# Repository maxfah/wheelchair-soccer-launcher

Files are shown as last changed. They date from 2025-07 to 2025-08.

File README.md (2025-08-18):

# Wheelchair Soccer Launcher

The completed wheelchair-mounted soccer ball launcher

This project is a soccer ball launcher designed to be mounted on a wheelchair. It was developed by students from the **[Waukee APEX Program](https://apex.waukeeschools.org/)** to support the amazing work of [**Can Play**](https://can-play.org/), a nonprofit organization dedicated to providing adaptive sports and recreation opportunities for children and adults with disabilities.

The goal of this project is to provide a low-cost, accessible, and replicable design that allows more individuals to participate in wheelchair soccer.

-----

## Images & Videos

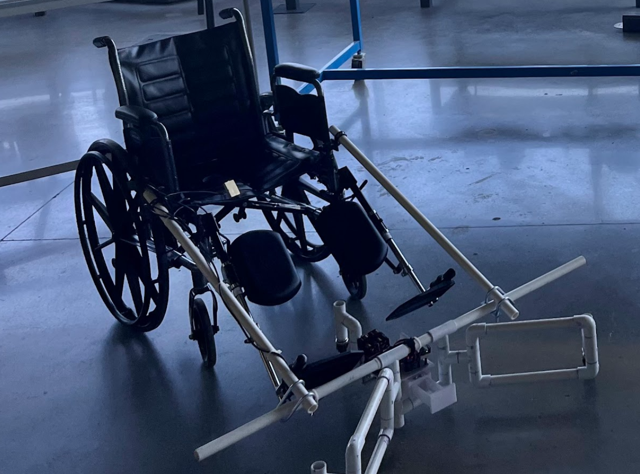
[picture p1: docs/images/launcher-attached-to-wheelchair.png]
The completed wheelchair-mounted soccer ball launcher attached to a wheelchair


All assembly images and demo videos are available below.

 * **[images](/docs/images/)**
 * **[videos](/docs/videos/)**

-----

## Documentation

All the files and instructions needed to build your own launcher can be found using the links below.

### Bill of Materials (BOM)

This document is split into two parts to make acquiring components as easy as possible. The **Project Component List** details every single part used in the final assembly. The **Purchase List** is a shopping list of the items you need to buy, often in packages that contain more parts than required for a single build.

  * **[bill-of-materials.md](/docs/bill-of-materials.md)**
  * **[bill-of-materials.xlsx](/docs/downloads/bill-of-materials.xlsx)** 

### Assembly Guide

A detailed, step-by-step guide with pictures covering the entire build process, from PVC cart assembly to final wiring.

  * **[assembly-guide.md](/docs/assembly-guide.md)**

### 3D Models

All 3D printable parts are available below. Files are available in `.step`, `.f3d`, `.3mf`, and individual `.stl` formats. The designs were created using Fusion 360.

  * **[3d-models](/3d-models/)**

### Code

All the MicroPython code for the Raspberry Pi Pico is located here. See the programming instructions in the Assembly Guide for how to load the code onto the Pico.

  * **[main.py](/micropython-code/)**

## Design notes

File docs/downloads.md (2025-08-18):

---
layout: default
title: Downloads
---

## Downloads

All the necessary design and code files for this project are available below. You can download everything in a single `.zip` package or browse the individual folders directly on GitHub.

The download includes all 3D printable parts (in `.stl`, `.step`, `.f3d`, and `.3mf` formats) designed in Fusion 360, as well as the MicroPython code for the Raspberry Pi Pico. Please see the Assembly Guide for instructions on how to load the code.

<a href="{{ site.baseurl }}/downloads/wheelchair-soccer-launcher-files.zip">Download All Project Files (.zip)</a>

---
### Browse Files on GitHub
* **3D Models:** [https://github.com/maxfah/wheelchair-soccer-launcher/tree/main/3d-models](https://github.com/maxfah/wheelchair-soccer-launcher/tree/main/3d-models)
* **MicroPython Code:** [https://github.com/maxfah/wheelchair-soccer-launcher/tree/main/micropython-code](https://github.com/maxfah/wheelchair-soccer-launcher/tree/main/micropython-code)

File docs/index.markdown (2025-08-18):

---
layout: default
---

# Wheelchair Soccer Launcher

The completed wheelchair-mounted soccer ball launcher

This project is a soccer ball launcher designed to be mounted on a wheelchair. It was developed by students from the **[Waukee APEX Program](https://apex.waukeeschools.org/)** to support the amazing work of [**Can Play**](https://can-play.org/), a nonprofit organization dedicated to providing adaptive sports and recreation opportunities for children and adults with disabilities.

The goal of this project is to provide a low-cost, accessible, and replicable design that allows more individuals to participate in wheelchair soccer.

-----

## Images & Videos

The completed wheelchair-mounted soccer ball launcher attached to a wheelchair

All assembly images and demo videos are available below.

* [**Media Gallery**](./media.html)

-----

## Documentation

All the files and instructions needed to build your own launcher can be found using the links below.

### Bill of Materials (BOM)

This document is split into two parts to make acquiring components as easy as possible. The **Project Component List** details every single part used in the final assembly. The **Purchase List** is a shopping list of the items you need to buy, often in packages that contain more parts than required for a single build.

* [**Bill of Materials**](./bill-of-materials.html)

### Assembly Guide

A detailed, step-by-step guide with pictures covering the entire build process, from PVC cart assembly to final wiring.

* [**Assembly Guide**](./assembly-guide.html)

### 3D Models & Code

All the necessary design and code files for this project can be found below. This includes all 3D printable parts (in `.stl`, `.step`, `.f3d`, and `.3mf` formats) designed in Fusion 3D, as well as the MicroPython code for the Raspberry Pi Pico. For instructions on how to load the code, please see the Assembly Guide.

* [**Downloads**](./downloads.html)

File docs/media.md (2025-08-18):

---
layout: default
title: Media Gallery
---

## Media Gallery

### Completed Project
Here are some photos of the finished launcher, both on its own and attached to a wheelchair.

<table>
  <tr>
    <td align="center">
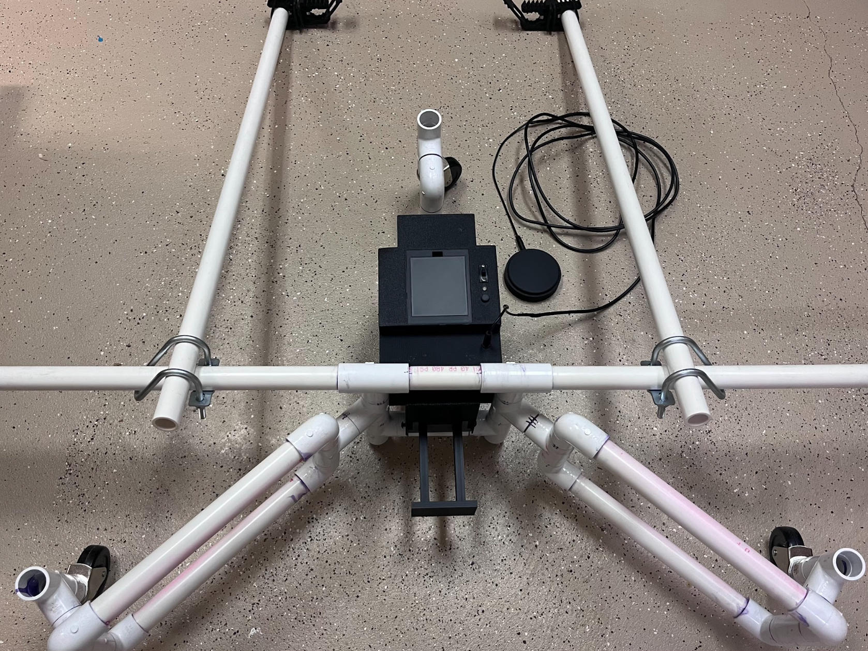
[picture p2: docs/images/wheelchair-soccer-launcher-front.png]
Finished launcher front view
      
      <br><sub>wheelchair-soccer-launcher-front.png</sub>
    </td>
    <td align="center">
      Finished launcher side view
      <br><sub>wheelchair-soccer-launcher-side.png</sub>
    </td>
    <td align="center">
      Launcher attached to a wheelchair
      <br><sub>launcher-attached-to-wheelchair.png</sub>
    </td>
  </tr>
</table>

### Videos
Here are some videos demonstrating the launcher's functionality.

**Launching a Ball**
<video width="100%" controls>
  <source src="{{ site.baseurl }}/videos/launching-ball.mp4" type="video/mp4">
  Your browser does not support the video tag.
</video>

**Testing Launcher Controls**
<video width="100%" controls>
  <source src="{{ site.baseurl }}/videos/testing-launcher-switches.mp4" type="video/mp4">
  Your browser does not support the video tag.
</video>

### Assembly Pictures
This gallery contains various pictures taken during the assembly process, showing close-ups of specific components and steps.

<table>
  <tr>
    <td align="center">
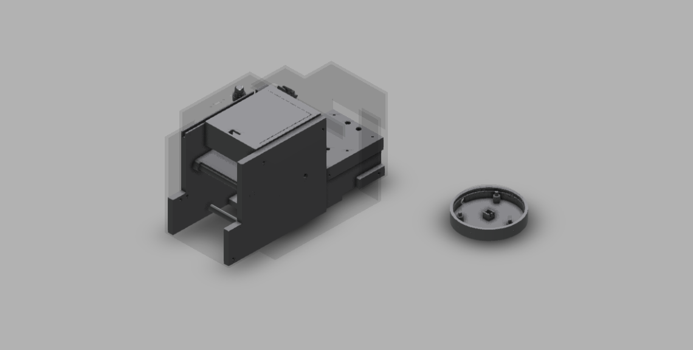
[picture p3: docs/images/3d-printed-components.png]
3D Printed Components
      
      <br><sub>3d-printed-components.png</sub>
    </td>
    <td align="center">
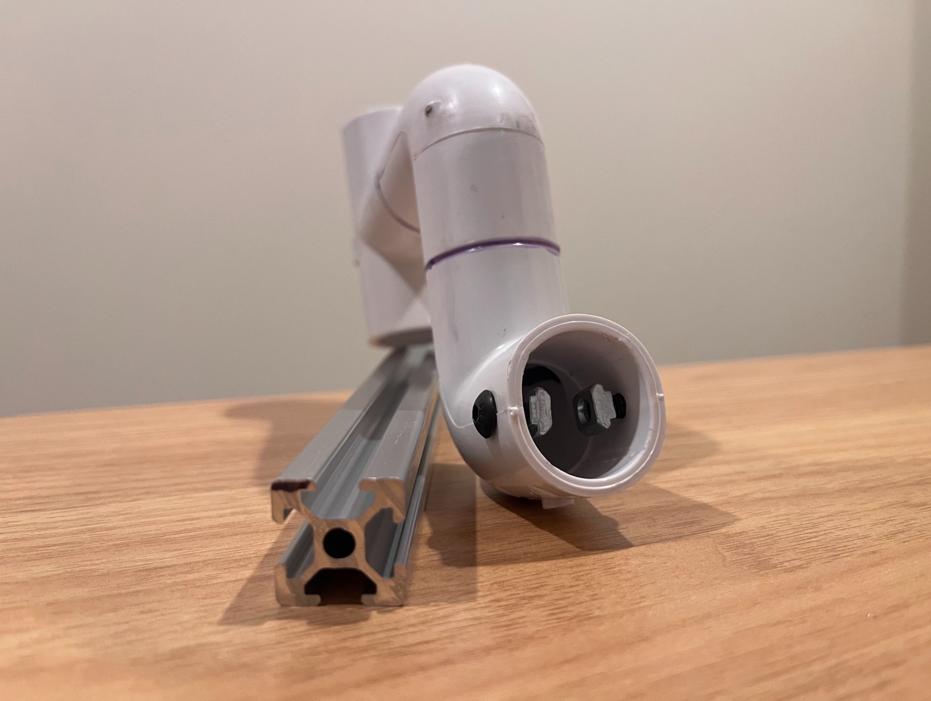
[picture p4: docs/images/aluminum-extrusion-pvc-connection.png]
Aluminum Extrusion PVC Connection
      
      <br><sub>aluminum-extrusion-pvc-connection.png</sub>
    </td>
    <td align="center">
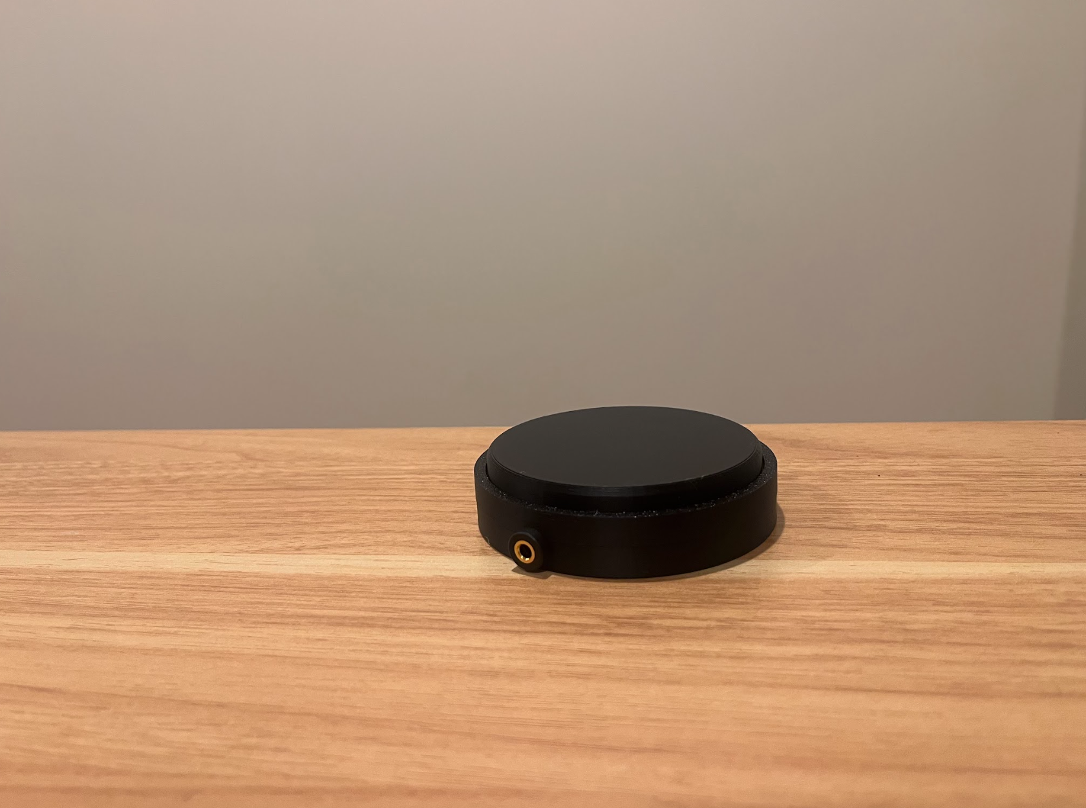
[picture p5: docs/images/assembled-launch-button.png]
Assembled Launch Button
      
      <br><sub>assembled-launch-button.png</sub>
    </td>
  </tr>
  <tr>
    <td align="center">
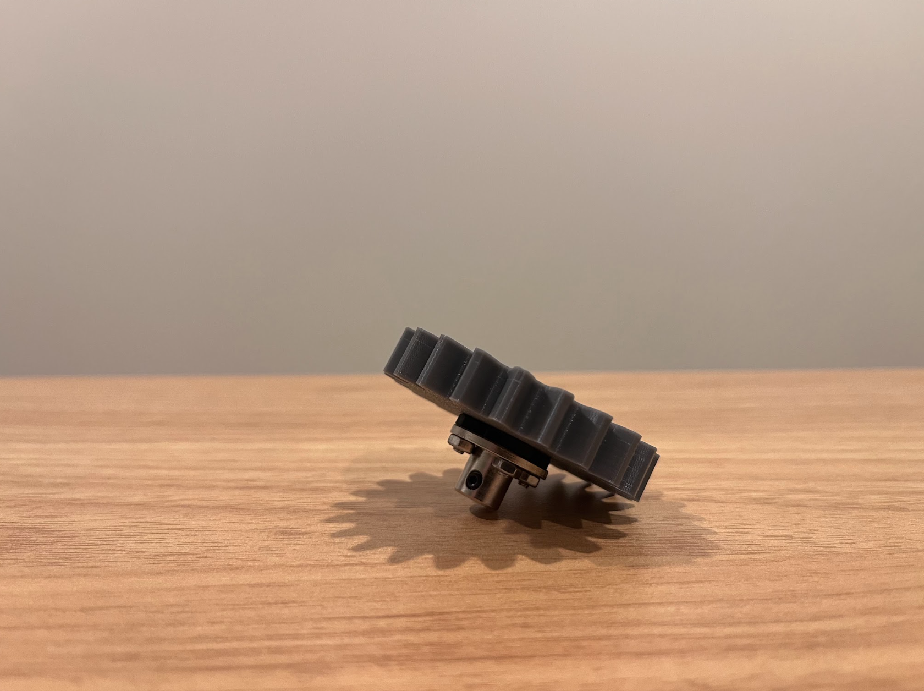
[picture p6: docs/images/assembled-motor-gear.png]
Assembled Motor Gear
      
      <br><sub>assembled-motor-gear.png</sub>
    </td>
    <td align="center">
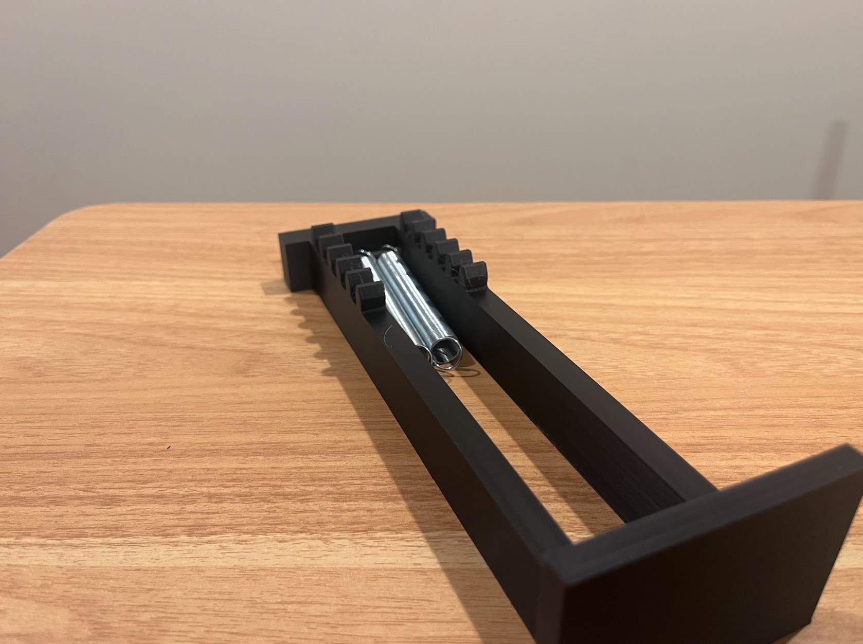
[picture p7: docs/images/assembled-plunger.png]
Assembled Plunger
      
      <br><sub>assembled-plunger.png</sub>
    </td>
    <td align="center">
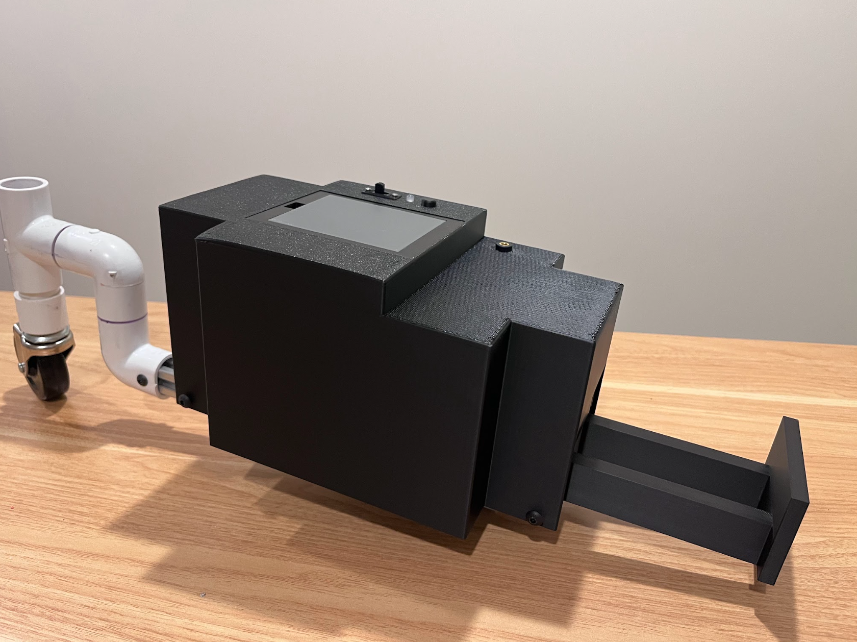
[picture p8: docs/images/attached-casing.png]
Attached Casing
      
      <br><sub>attached-casing.png</sub>
    </td>
  </tr>
  <tr>
    <td align="center">
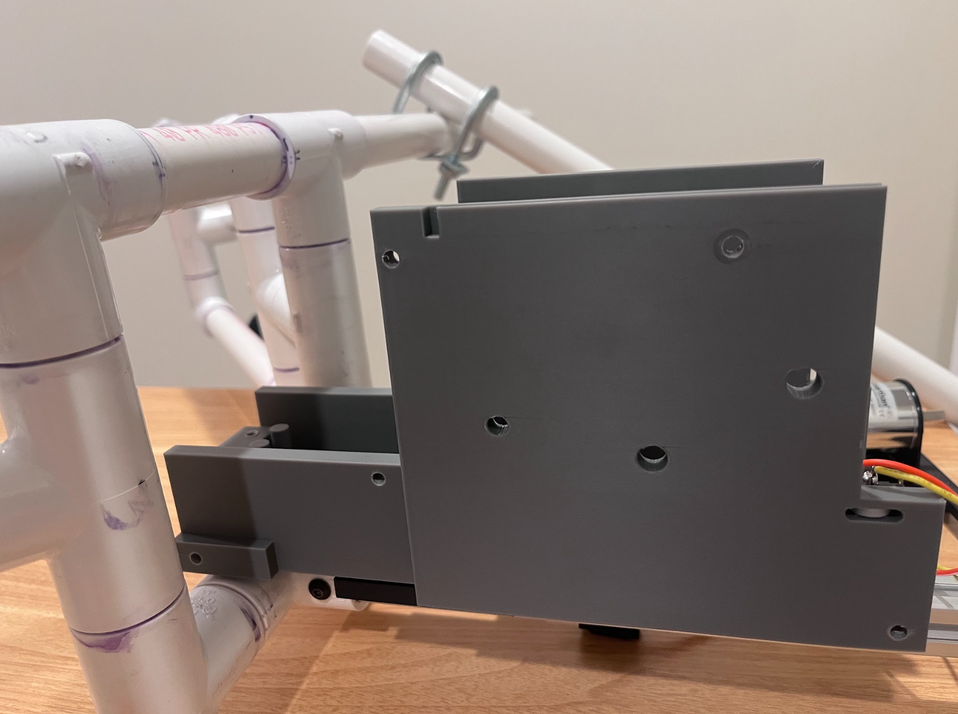
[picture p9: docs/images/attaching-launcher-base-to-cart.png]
Attaching Launcher Base to Cart
      
      <br><sub>attaching-launcher-base-to-cart.png</sub>
    </td>
    <td align="center">
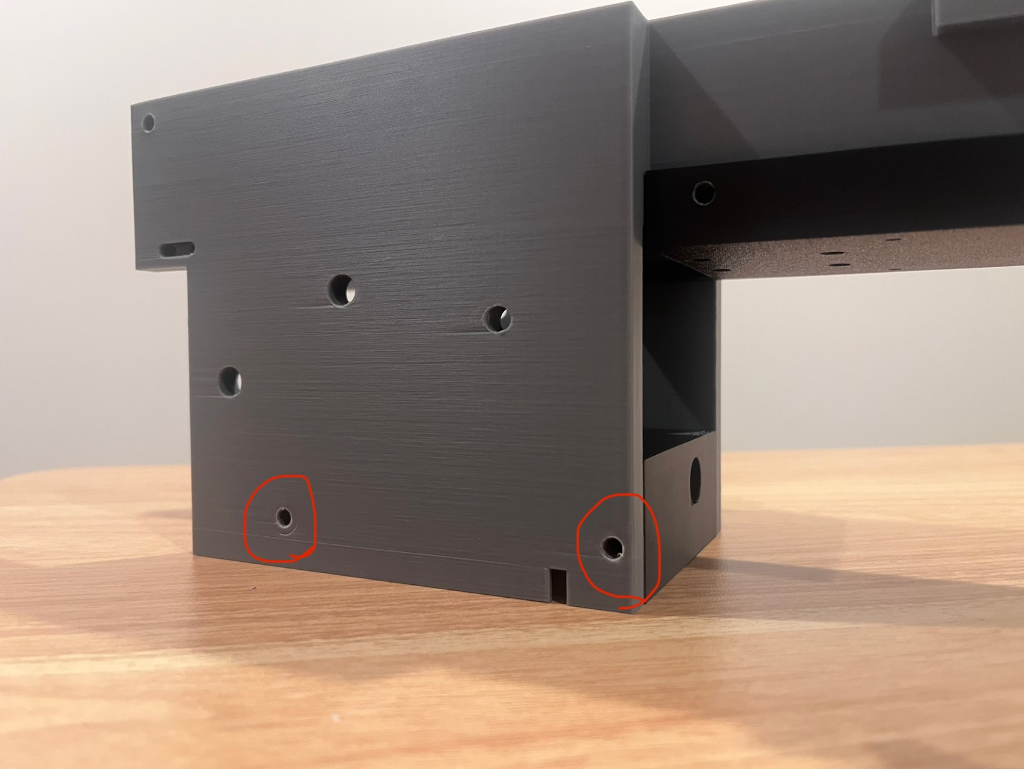
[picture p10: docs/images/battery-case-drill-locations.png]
Battery Case Drill Locations
      
      <br><sub>battery-case-drill-locations.png</sub>
    </td>
    <td align="center">
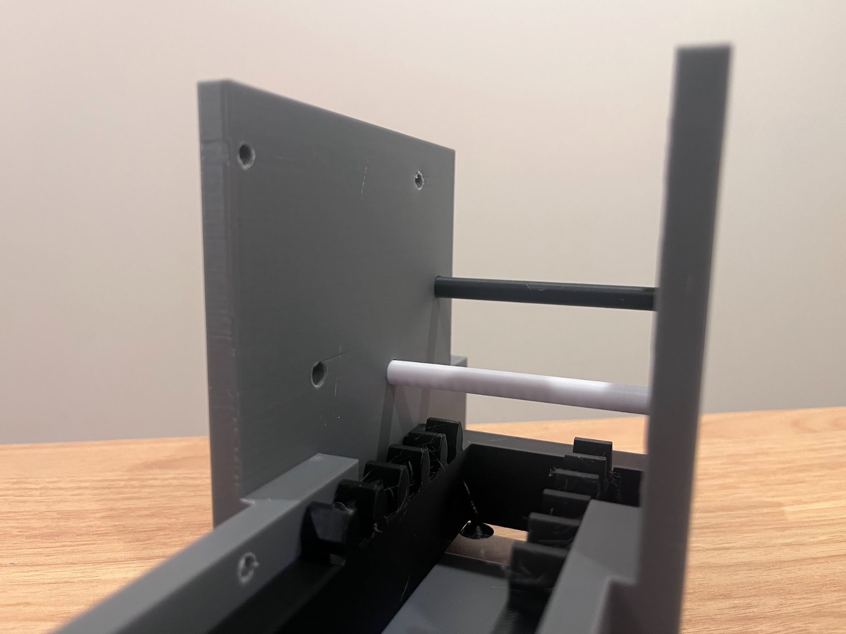
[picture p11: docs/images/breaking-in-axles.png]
Breaking In Axles
      
      <br><sub>breaking-in-axles.png</sub>
    </td>
  </tr>
  <tr>
    <td align="center">
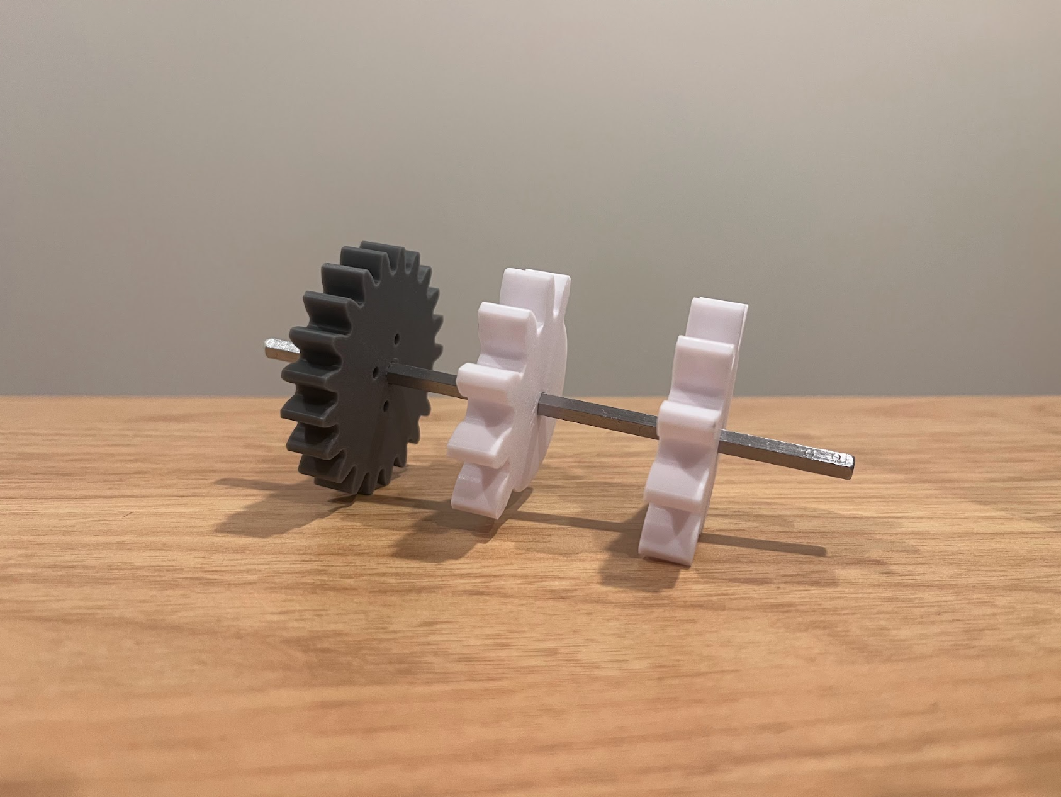
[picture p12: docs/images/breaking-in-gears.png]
Breaking In Gears
      
      <br><sub>breaking-in-gears.png</sub>
    </td>
    <td align="center">
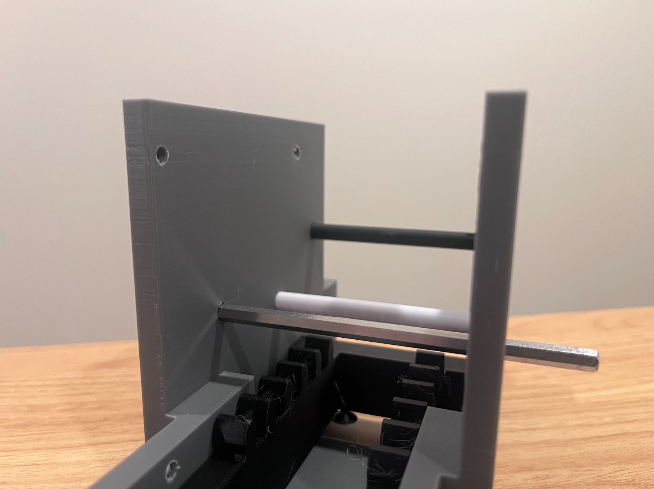
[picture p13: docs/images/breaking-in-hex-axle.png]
Breaking In Hex Axle
      
      <br><sub>breaking-in-hex-axle.png</sub>
    </td>
    <td align="center">
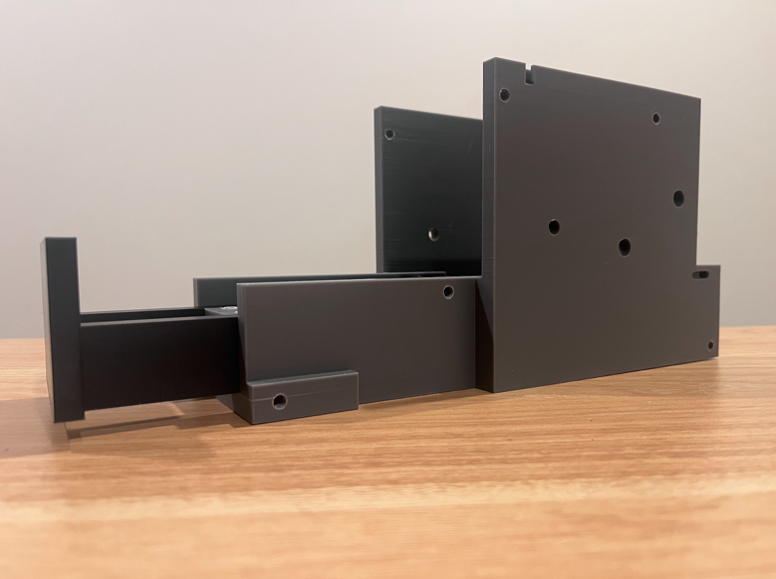
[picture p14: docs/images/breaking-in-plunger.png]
Breaking In Plunger
      
      <br><sub>breaking-in-plunger.png</sub>
    </td>
  </tr>
  <tr>
    <td align="center">
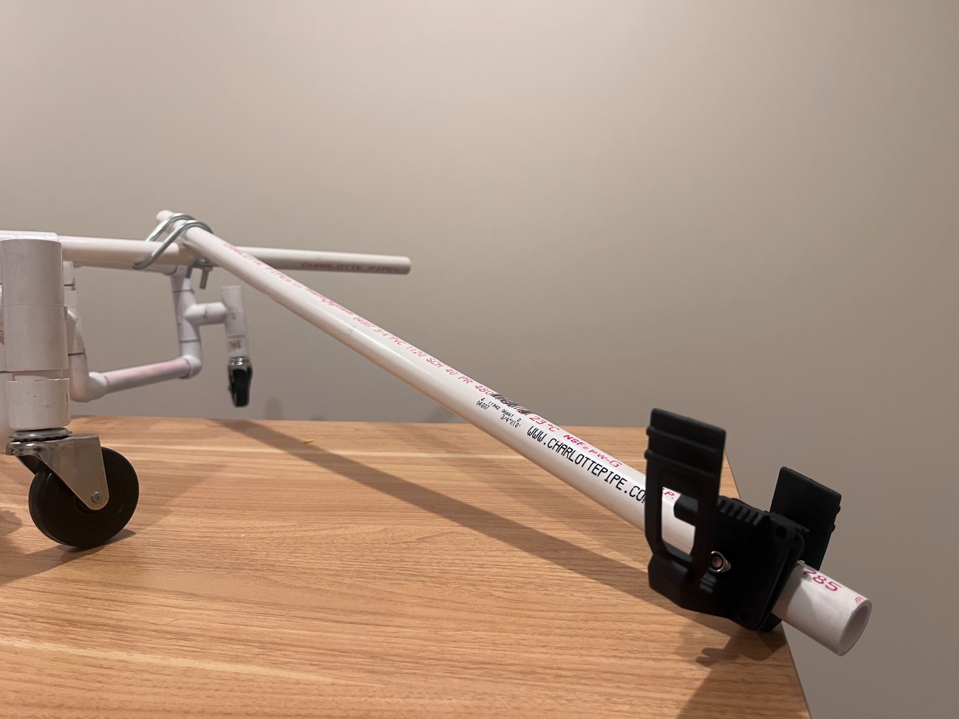
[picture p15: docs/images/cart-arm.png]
Cart Arm
      
      <br><sub>cart-arm.png</sub>
    </td>
    <td align="center">
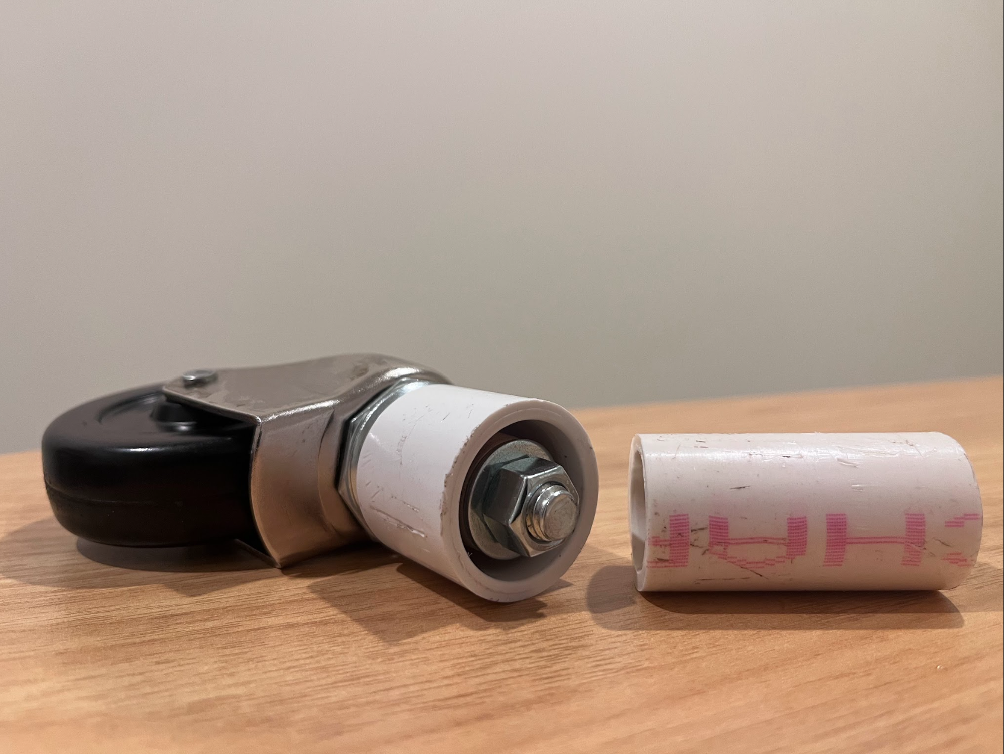
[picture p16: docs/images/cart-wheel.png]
Cart Wheel
      
      <br><sub>cart-wheel.png</sub>
    </td>
    <td align="center">
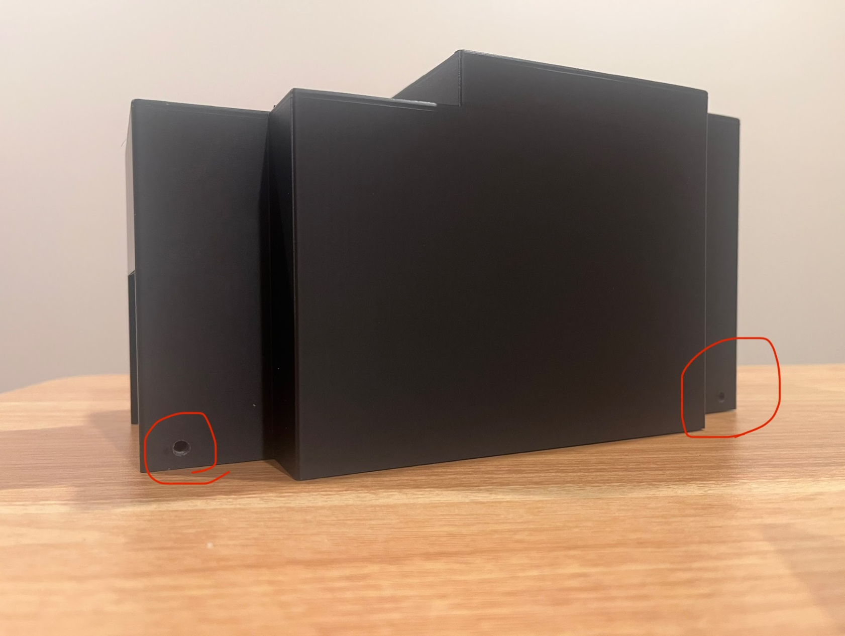
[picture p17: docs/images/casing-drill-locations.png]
Casing Drill Locations
      
      <br><sub>casing-drill-locations.png</sub>
    </td>
  </tr>
  <tr>
    <td align="center">
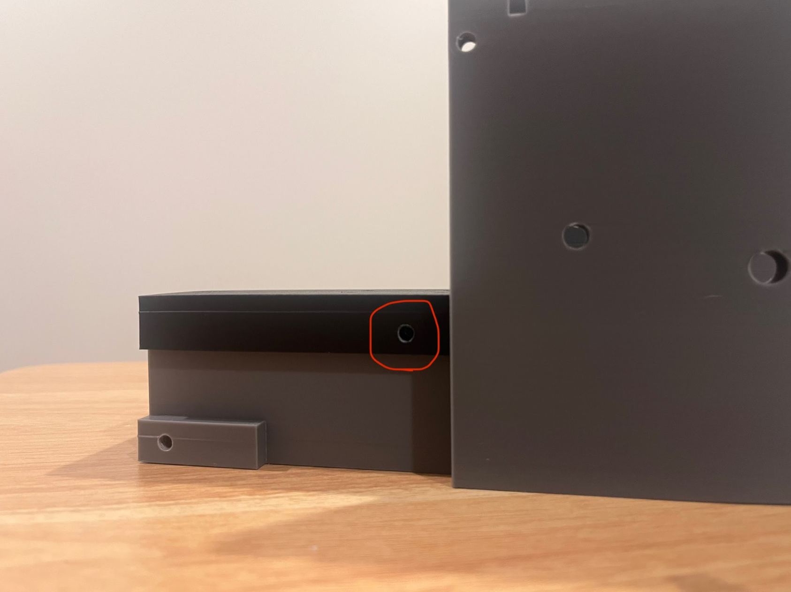
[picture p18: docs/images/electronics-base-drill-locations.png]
Electronics Base Drill Locations
      
      <br><sub>electronics-base-drill-locations.png</sub>
    </td>
    <td align="center">
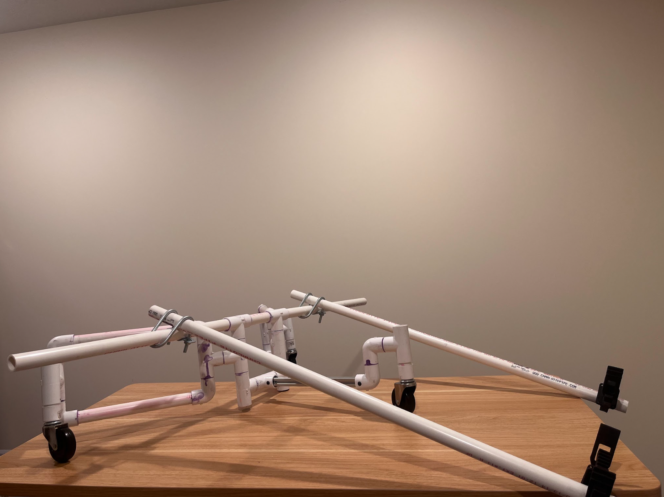
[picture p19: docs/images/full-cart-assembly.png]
Full Cart Assembly
      
      <br><sub>full-cart-assembly.png</sub>
    </td>
    <td align="center">
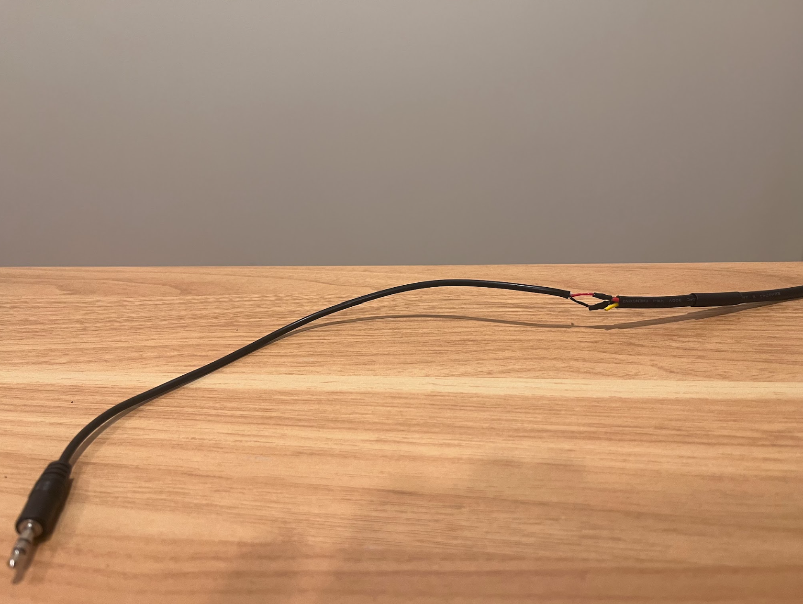
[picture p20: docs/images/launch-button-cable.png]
Launch Button Cable
      
      <br><sub>launch-button-cable.png</sub>
    </td>
  </tr>
  <tr>
    <td align="center">
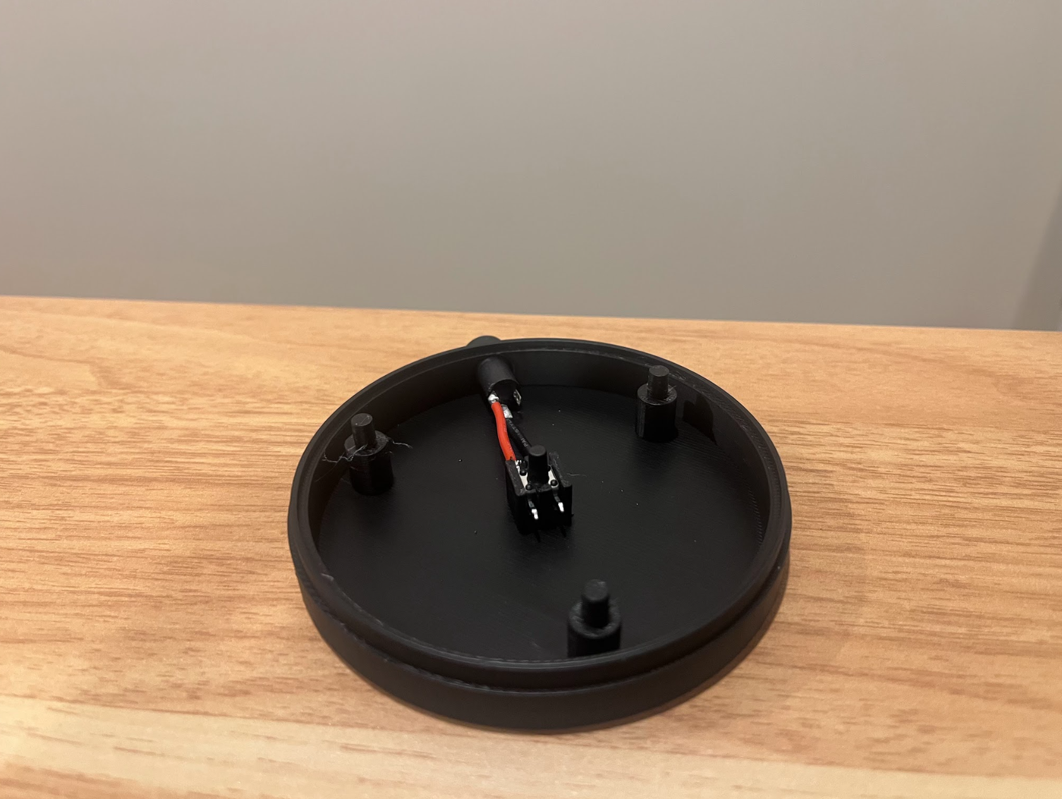
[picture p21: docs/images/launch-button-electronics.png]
Launch Button Electronics
      
      <br><sub>launch-button-electronics.png</sub>
    </td>
    <td align="center">
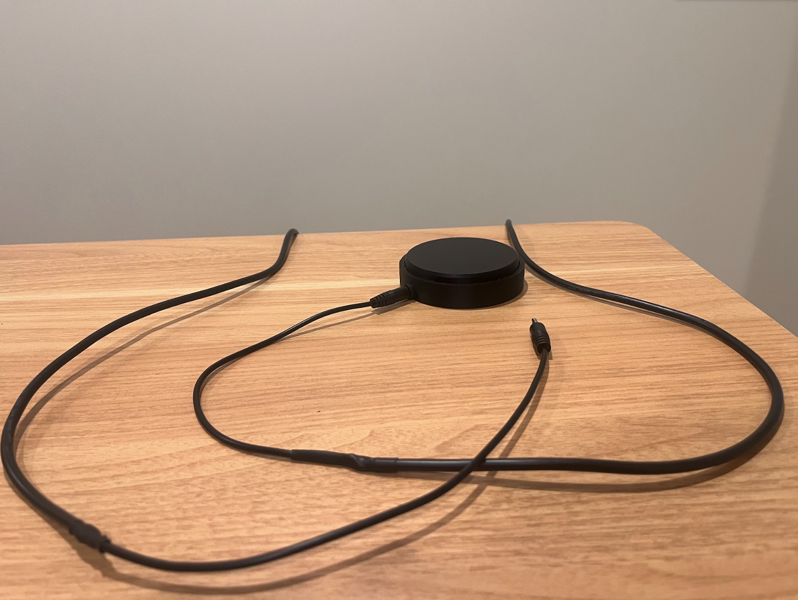
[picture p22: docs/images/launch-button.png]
Launch Button
      
      <br><sub>launch-button.png</sub>
    </td>
    <td align="center">
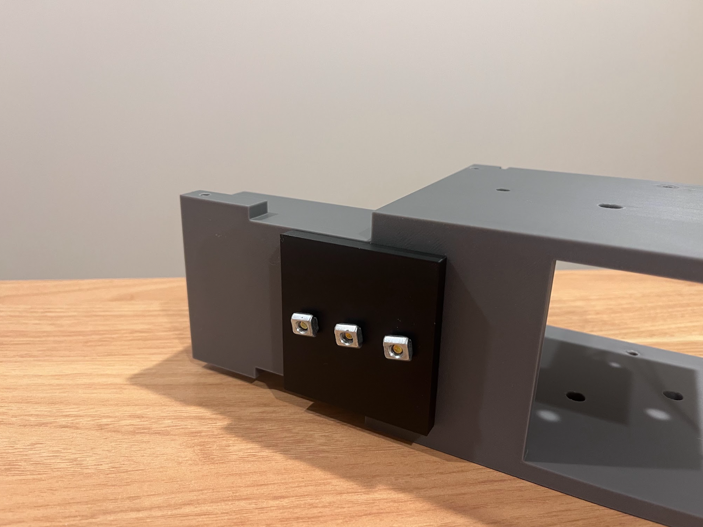
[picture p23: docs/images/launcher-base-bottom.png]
Launcher Base Bottom
      
      <br><sub>launcher-base-bottom.png</sub>
    </td>
  </tr>
  <tr>
    <td align="center">
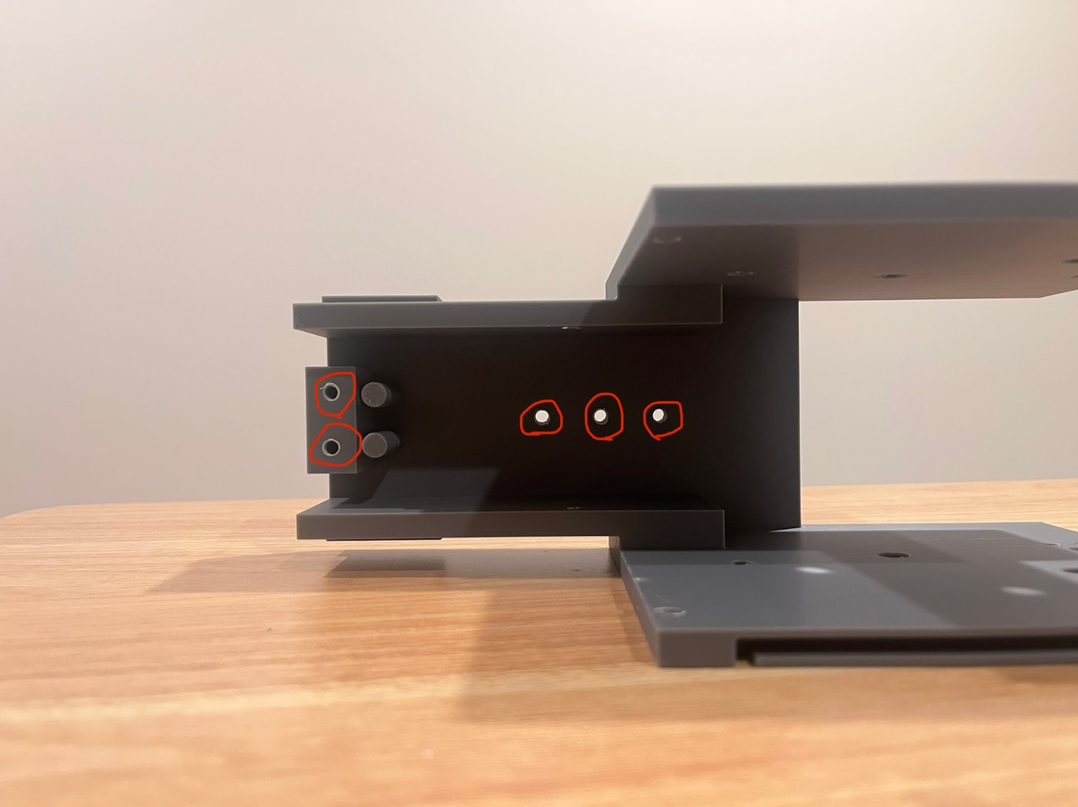
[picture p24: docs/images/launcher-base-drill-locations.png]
Launcher Base Drill Locations
      
      <br><sub>launcher-base-drill-locations.png</sub>
    </td>
    <td align="center">
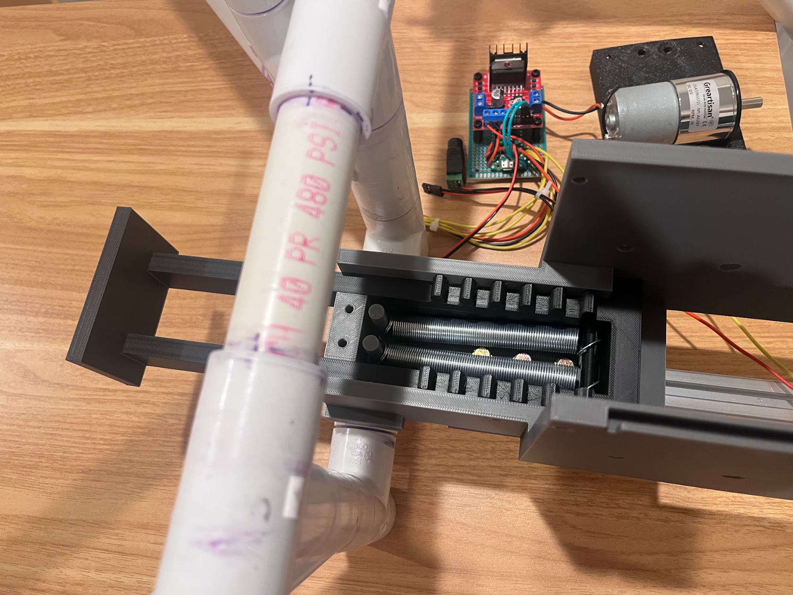
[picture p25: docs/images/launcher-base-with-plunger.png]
Launcher Base with Plunger
      
      <br><sub>launcher-base-with-plunger.png</sub>
    </td>
    <td align="center">
      Launcher Circuit
      <br><sub>launcher-circuit.png</sub>
    </td>
  </tr>
  <tr>
    <td align="center">
      Main Cart Frame Design
      <br><sub>main-cart-frame-design.png</sub>
    </td>
    <td align="center">
      Main Control Board
      <br><sub>main-control-board.png</sub>
    </td>
    <td align="center">
      Mounted Batteries
      <br><sub>mounted-batteries.png</sub>
    </td>
  </tr>
  <tr>
    <td align="center">
      Mounted Battery Case
      <br><sub>mounted-battery-case.png</sub>
    </td>
    <td align="center">
      Mounted Control Board
      <br><sub>mounted-control-board.png</sub>
    </td>
    <td align="center">
      Mounted Electronics Base
      <br><sub>mounted-electronics-base.png</sub>
    </td>
  </tr>
  <tr>
    <td align="center">
      Mounted Hex Shaft
      <br><sub>mounted-hex-shaft.png</sub>
    </td>
    <td align="center">
      Mounted Motor Gear
      <br><sub>mounted-motor-gear.png</sub>
    </td>
    <td align="center">
      Mounted Pawl
      <br><sub>mounted-pawl.png</sub>
    </td>
  </tr>
  <tr>
    <td align="center">
      Mounting Limit Switch
      <br><sub>mounting-limit-switch.png</sub>
    </td>
    <td align="center">
      Mounting Motor
      <br><sub>mounting-motor.png</sub>
    </td>
    <td align="center">
      PVC Drill Locations
      <br><sub>pvc-drill-locations.png</sub>
    </td>
  </tr>
  <tr>
    <td align="center">
      Testing Electronics
      <br><sub>testing-electronics.png</sub>
    </td>
    <td align="center">
      Wheelchair Grip
      <br><sub>wheelchair-grip.png</sub>
    </td>
    <td align="center">
      Wiring Casing
      <br><sub>wiring-casing.png</sub>
    </td>
  </tr>
  <tr>
    <td align="center">
      Wiring L298N
      <br><sub>wiring-l298n.png</sub>
    </td>
    <td align="center">
      Wiring Pico
      <br><sub>wiring-pico.png</sub>
    </td>
    <td align="center">
    </td>
  </tr>
</table>

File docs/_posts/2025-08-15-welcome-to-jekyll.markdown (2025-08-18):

---
layout: post
title:  "Welcome to Jekyll!"
date:   2025-08-15 19:27:29 -0500
categories: jekyll update
---
You’ll find this post in your `_posts` directory. Go ahead and edit it and re-build the site to see your changes. You can rebuild the site in many different ways, but the most common way is to run `jekyll serve`, which launches a web server and auto-regenerates your site when a file is updated.

Jekyll requires blog post files to be named according to the following format:

`YEAR-MONTH-DAY-title.MARKUP`

Where `YEAR` is a four-digit number, `MONTH` and `DAY` are both two-digit numbers, and `MARKUP` is the file extension representing the format used in the file. After that, include the necessary front matter. Take a look at the source for this post to get an idea about how it works.

Jekyll also offers powerful support for code snippets:

{% highlight ruby %}
def print_hi(name)
  puts "Hi, #{name}"
end
print_hi('Tom')
#=> prints 'Hi, Tom' to STDOUT.
{% endhighlight %}

Check out the [Jekyll docs][jekyll-docs] for more info on how to get the most out of Jekyll. File all bugs/feature requests at [Jekyll’s GitHub repo][jekyll-gh]. If you have questions, you can ask them on [Jekyll Talk][jekyll-talk].

[jekyll-docs]: https://jekyllrb.com/docs/home
[jekyll-gh]:   https://github.com/jekyll/jekyll
[jekyll-talk]: https://talk.jekyllrb.com/

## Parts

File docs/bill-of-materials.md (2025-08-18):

---
layout: default
title: Bill of Materials
---

## Project Component List

This list details every individual component required for the project, along with its calculated cost based on the package price.

<a href="{{ site.baseurl }}/downloads/bill-of-materials.xlsx">Download Original Spreadsheet (.xlsx)</a>

### Electronics

| Item | Source | Quantity | Unit of Measure | Unit Cost | Total Project Cost |
| :--- | :--- | :--- | :--- | :--- | :--- |
| 11' 20 AWG 3-Conductor Electrical Wire | [33' 20 AWG 3-Conductor Electrical Wire](https://a.co/d/fJsRZCa) | 1 | ea | $5.33 | $5.33 |
| 18650 Battery Case Holder | [18650 Battery Case Holder](https://a.co/d/0sHe8RC) | 1 | ea | $4.00 | $4.00 |
| 18650 Rechargeable Batteries | [18650 Rechargeable Batteries with Charger (4-pack)](https://a.co/d/61mFCPq) | 3 | ea | $5.50 | $16.50 |
| 2 Pin Housing Connector | [Dupont Connector Kit (600 pcs)](https://a.co/d/eYwAEnl) | 1 | ea | $0.02 | $0.02 |
| 3.5mm Female Mount Jack | [3.5mm Female Mount Jack (3-pack)](https://a.co/d/40ZtWEH) | 2 | ea | $2.33 | $4.66 |
| 3.5mm Male Plug Jack Connector | [3.5mm Male Jack Connector (2-pack)](https://a.co/d/iWRQpHo) | 2 | ea | $2.75 | $5.50 |
| 470 Ω Resistor | [470 Ω Resistors (100 pcs)](https://a.co/d/aYIXwVM) | 1 | ea | $0.06 | $0.06 |
| 5 Pin Housing Connector | [Dupont Connector Kit (600 pcs)](https://a.co/d/eYwAEnl) | 2 | ea | $0.02 | $0.04 |
| 5.5mm Female DC Barrel Connector | [12V 2.1mm x 5.5mm DC Power Jack Adapter (4-pack)](https://a.co/d/751q0LK) | 1 | ea | $0.99 | $0.99 |
| 5cm x 7cm PCB Board | [PCB Boards (32 pcs)](https://a.co/d/8yXHcdF) | 1 | ea | $0.22 | $0.22 |
| DC Motor | [Greartisan DC 12V 30RPM Gear Motor](https://a.co/d/9EDaZ5f) | 1 | ea | $15.99 | $15.99 |
| Female Pin Connector | [Dupont Connector Kit (600 pcs)](https://a.co/d/eYwAEnl) | 7 | ea | $0.02 | $0.14 |
| Limit Switch | [Micro Limit Switch (1-pack)](https://a.co/d/icHqxsF) | 1 | ea | $3.99 | $3.99 |
| Male Pin Connector | [Dupont Connector Kit (600 pcs)](https://a.co/d/eYwAEnl) | 5 | ea | $0.02 | $0.10 |
| L298N Motor Driver | [L298N H Bridge Stepper Motor Driver](https://a.co/d/d2QPwzO) | 1 | ea | $2.50 | $2.50 |
| Raspberry Pi Pico | [Raspberry Pi Pico H - Pico with Headers Soldered](https://www.adafruit.com/product/5525) | 1 | ea | $5.00 | $5.00 |
| RGB 5mm LED | [RGB 5mm Tri-Color LEDs](https://a.co/d/4jlZoVg) | 1 | ea | $0.09 | $0.09 |
| Slide Switch | [Compact Slide Switch](https://a.co/d/2EBehJg) | 1 | ea | $3.99 | $3.99 |
| 6x6x9.5mm Tactile Push Button Switch | [Tactile Push Button Switches (180 pcs)](https://a.co/d/5Mcb5Zq) | 1 | ea | $0.05 | $0.05 |
| 6x6x11mm Tactile Push Button Switch | [Tactile Push Button Switches (180 pcs)](https://a.co/d/5Mcb5Zq) | 1 | ea | $0.05 | $0.05 |

### Fasteners & Hardware

| Item | Source | Quantity | Unit of Measure | Unit Cost | Total Project Cost |
| :--- | :--- | :--- | :--- | :--- | :--- |
| 3/8"-16 Coarse Thread Hex Nut | [3/8"-16 Zinc Plated Coarse Thread Hex Nut (8-pack)](https://www.menards.com/main/hardware/fasteners-connectors/nuts/hex-jam-nuts/grip-fast-reg-blue-zinc-grade-2-coarse-thread-hex-nuts/zhn38-8/p-1444421582846-c-8915.htm) | 3 | ea | $0.13 | $0.39 |
| 3/8" Flat Washer | [3/8" Zinc Plated Flat Washer (24-pack)](https://www.menards.com/main/hardware/fasteners-connectors/washers-spacers/flat-washers/grip-fast-reg-3-8-grade-2-a307-zinc-flat-washer-24-count/15073/p-1444439719658-c-8945.htm) | 3 | ea | $0.07 | $0.21 |
| M3 (15mm + 6mm) Single Head Standoff | [M3 Standoff Kit (320 pcs)](https://a.co/d/gYZp2mI) | 2 | ea | $0.03 | $0.06 |
| M3 (15mm) Double-Pass Standoff | [M3 Standoff Kit (320 pcs)](https://a.co/d/gYZp2mI) | 6 | ea | $0.03 | $0.18 |
| M3 Coupler Fastening Screw | [6mm Flange Shaft Coupler (5-pack)](https://a.co/d/dtI1bwZ) | 3 | ea | $0.20 | $0.60 |
| M3 Coupler Nut | [6mm Flange Shaft Coupler (5-pack)](https://a.co/d/dtI1bwZ) | 4 | ea | $0.20 | $0.80 |
| M3 Standoff Nut | [M3 Standoff Kit (320 pcs)](https://a.co/d/gYZp2mI) | 4 | ea | $0.03 | $0.12 |
| M3 x 12mm Standoff Screw | [M3 Standoff Kit (320 pcs)](https://a.co/d/gYZp2mI) | 4 | ea | $0.03 | $0.12 |
| M3 x 14mm Coupler Socket Head Cap Screw | [6mm Flange Shaft Coupler (5-pack)](https://a.co/d/dtI1bwZ) | 4 | ea | $0.20 | $0.80 |
| M3 x 6mm Standoff Screw | [M3 Standoff Kit (320 pcs)](https://a.co/d/gYZp2mI) | 8 | ea | $0.03 | $0.24 |
| M3 Washer | [M3 Standoff Kit (320 pcs)](https://a.co/d/gYZp2mI) | 4 | ea | $0.03 | $0.12 |
| M5 Flat Washer | [Assorted Nuts and Bolts Kit (720 pcs)](https://www.amazon.com/720pcs-Metric-Assortment-Yellow-Plated/dp/B0BYNLV7YG?ref_=ast_sto_dp&th=1) | 5 | ea | $0.04 | $0.20 |
| M5 Nut | [Assorted Nuts and Bolts Kit (720 pcs)](https://www.amazon.com/720pcs-Metric-Assortment-Yellow-Plated/dp/B0BYNLV7YG?ref_=ast_sto_dp&th=1) | 4 | ea | $0.04 | $0.16 |
| M5 T Nut | [M5 Screws and T Nuts Kit (420 pcs)](https://a.co/d/blOClPc) | 7 | ea | $0.04 | $0.28 |
| M5 x 8mm Screw | [M5 Screws and T Nuts Kit (420 pcs)](https://a.co/d/blOClPc) | 6 | ea | $0.04 | $0.24 |
| M5 x 10mm Screw | [M5 Screws and T Nuts Kit (420 pcs)](https://a.co/d/blOClPc) | 4 | ea | $0.04 | $0.16 |
| M5 x 12mm Screw | [M5 Screws and T Nuts Kit (420 pcs)](https://a.co/d/blOClPc) | 4 | ea | $0.04 | $0.16 |
| M5 x 14mm Screw | [M5 Screws and T Nuts Kit (420 pcs)](https://a.co/d/blOClPc) | 4 | ea | $0.04 | $0.16 |
| M5 x 25mm Bolt | [Assorted Nuts and Bolts Kit (720 pcs)](https://www.amazon.com/720pcs-Metric-Assortment-Yellow-Plated/dp/B0BYNLV7YG?ref_=ast_sto_dp&th=1) | 3 | ea | $0.04 | $0.12 |
| M5 x 30mm Bolt | [Assorted Nuts and Bolts Kit (720 pcs)](https://www.amazon.com/720pcs-Metric-Assortment-Yellow-Plated/dp/B0BYNLV7YG?ref_=ast_sto_dp&th=1) | 2 | ea | $0.04 | $0.08 |
| M6 Flat Washer | [Assorted Nuts and Bolts Kit (720 pcs)](https://www.amazon.com/720pcs-Metric-Assortment-Yellow-Plated/dp/B0BYNLV7YG?ref_=ast_sto_dp&th=1) | 6 | ea | $0.04 | $0.24 |
| M6 Nylon Lock Nut | [M6 x 1mm Nylon Lock Nuts (35 pcs)](https://a.co/d/dPlYyLJ) | 2 | ea | $0.16 | $0.32 |
| M6 x 30mm Bolt | [Assorted Nuts and Bolts Kit (720 pcs)](https://www.amazon.com/720pcs-Metric-Assortment-Yellow-Plated/dp/B0BYNLV7YG?ref_=ast_sto_dp&th=1) | 2 | ea | $0.04 | $0.08 |

### Structural & Mechanical

| Item | Source | Quantity | Unit of Measure | Unit Cost | Total Project Cost |
| :--- | :--- | :--- | :--- | :--- | :--- |
| 1/2" x 3-13/16" Extension Springs | [1/2" x 3-13/16" Zinc Extension Spring](https://www.menards.com/main/hardware/fasteners-connectors/specialty-fasteners/springs/midwest-fastener-reg-1-2-x-3-13-16-zinc-extension-spring-1-count/88121/p-1444440197466-c-9553.htm) | 2 | ea | $2.39 | $4.78 |
| 11.8" (300mm) 200 T Slot Aluminum Extrusion | [300mm 2020 T Slot Aluminum Extrusions (4 pcs)](https://a.co/d/22snyCf) | 1 | ea | $6.00 | $6.00 |
| 2-1/2" Soft Rubber Swivel Caster Wheel | [2-1/2" Soft Rubber Swivel Caster Wheel w/ 3/8"-16 x 1-1/2" threaded swivel stem](https://www.menards.com/main/hardware/casters-furniture-hardware/casters/shepherd-hardware-reg-2-1-2-soft-rubber-swivel-caster-wheel/9340m/p-1444442245967-c-13090.htm?exp=false) | 3 | ea | $4.49 | $13.47 |
| 3/4" x 1" Wood Dowel | [3/4" x 48" Round Poplar Dowel](https://www.menards.com/main/doors-windows-millwork/dowels-wooden-pins-plugs/madison-mill-round-poplar-dowels/436578/p-1444438758494-c-12188.htm) | 3 | ea | $0.07 | $0.21 |
| 3/4" x 11" PVC Pipe | [3/4" x 10' SDR 21 PVC Plain End Pressure Pipe](https://www.menards.com/main/plumbing/pipe-fittings/pvc-pipe-fittings/sdr21-pvc-pressure-pipe/pvc200070600hc/p-1444426399617-c-8571.htm?missingVariation=true) | 4 | ea | $0.39 | $1.56 |
| 3/4" x 2" PVC Pipe | [3/4" x 10' SDR 21 PVC Plain End Pressure Pipe](https://www.menards.com/main/plumbing/pipe-fittings/pvc-pipe-fittings/sdr21-pvc-pressure-pipe/pvc200070600hc/p-1444426399617-c-8571.htm?missingVariation=true) | 23 | ea | $0.07 | $1.61 |
| 3/4" x 20" PVC Pipe | [3/4" x 10' SDR 21 PVC Plain End Pressure Pipe](https://www.menards.com/main/plumbing/pipe-fittings/pvc-pipe-fittings/sdr21-pvc-pressure-pipe/pvc200070600hc/p-1444426399617-c-8571.htm?missingVariation=true) | 2 | ea | $0.72 | $1.44 |
| 3/4" x 36" PVC Pipe | [3/4" x 10' SDR 21 PVC Plain End Pressure Pipe](https://www.menards.com/main/plumbing/pipe-fittings/pvc-pipe-fittings/sdr21-pvc-pressure-pipe/pvc200070600hc/p-1444426399617-c-8571.htm?missingVariation=true) | 2 | ea | $1.29 | $2.58 |
| 3/4" x 5" PVC Pipe | [3/4" x 10' SDR 21 PVC Plain End Pressure Pipe](https://www.menards.com/main/plumbing/pipe-fittings/pvc-pipe-fittings/sdr21-pvc-pressure-pipe/pvc200070600hc/p-1444426399617-c-8571.htm?missingVariation=true) | 1 | ea | $0.18 | $0.18 |
| 3/4" Socket PVC 90-Degree Elbow | [3/4" Socket Sch 40 PVC 90-Degree Elbow](https://www.menards.com/main/plumbing/pipe-fittings/pvc-pipe-fittings/nibco-reg-socket-schedule-40-pvc-90-degree-elbow/f01680d/p-1444449163717-c-8571.htm?exp=false) | 10 | ea | $0.67 | $6.70 |
| 3/4" Socket PVC Cap | [3/4" Socket Sch 40 PVC Cap](https://www.menards.com/main/plumbing/pipe-fittings/pvc-pipe-fittings/nibco-reg-socket-schedule-40-pvc-cap/f01890d/p-1444449177939-c-8571.htm?exp=false) | 3 | ea | $0.81 | $2.43 |
| 3/4" Socket PVC Tee | [3/4" Socket Sch 40 PVC Tee](https://www.menards.com/main/plumbing/pipe-fittings/pvc-pipe-fittings/nibco-reg-socket-schedule-40-pvc-tee/f01790d/p-1444449168936-c-8571.htm?exp=false) | 14 | ea | $0.86 | $12.04 |
| 37mm Motor Mounting Bracket | [uxcell 37mm Motor Mounting Bracket](https://a.co/d/i3AjQt8) | 1 | ea | $10.69 | $10.69 |
| 3D Printed Components | [SUNLU PLA+2.0 Filament (1kg spool)](https://a.co/d/5zXOyYR) | 829.41 | g | $0.02 | $16.59 |
| 4" Zip Ties | [4" Zip Ties (200-pack)](https://a.co/d/fQBFUen) | 3 | ea | $0.02 | $0.06 |
| 5mm x 135mm Hex Shaft | [5mm x 135mm Hex Shaft (4-pack)](https://www.revrobotics.com/5mm-Hex-Shafts/) | 1 | ea | $4.25 | $4.25 |
| 6mm Flange Coupler | [6mm Flange Shaft Coupler (5-pack)](https://a.co/d/dtI1bwZ) | 3 | ea | $0.20 | $0.60 |
| Cross Connector Pipe Clip | [1-1/4" O.D. Cross-Connector Pipe Clip](https://a.co/d/65sJAJZ) | 2 | ea | $2.30 | $4.60 |
| QUICK FIST Mini Clamp 5/8' - 1-3/8' | [QUICK FIST Mini Clamp 5/8" - 1-3/8" (2-pack)](https://www.amazon.com/dp/B006NOC8Q6?th=1) | 4 | ea | $4.48 | $17.92 |
| Rubber Band | [Rubber Bands](https://a.co/d/6Yn3jlO) | 1 | ea | $0.02 | $0.02 |

### Consumables

| Item | Source | Quantity | Unit of Measure | Unit Cost | Total Project Cost |
| :--- | :--- | :--- | :--- | :--- | :--- |
| 20 AWG Wire | [20 AWG Wire](https://a.co/d/efYaxqC) | 10 | ft | $0.15 | $1.50 |
| 4mm Wire Heat Shrink Tubing | [Wire Heat Shrink Tubing Kit (900 pcs)](https://a.co/d/6wIdCTN) | 10 | ea | $0.01 | $0.10 |
| 6mm Wire Heat Shrink Tubing | [Wire Heat Shrink Tubing Kit (900 pcs)](https://a.co/d/6wIdCTN) | 10 | ea | $0.01 | $0.10 |
| PVC Primer & Cement | [All-Purpose Pipe Cement and Purple Primer Pack - 4 oz](https://www.menards.com/main/plumbing/plumbing-installation-repair/pipe-cements-cleaners-primers/oatey-reg-all-purpose-cement-and-purple-primer-handy-pack-4-oz/302505/p-1958440145915521-c-8530.htm) | 6 | oz | $1.25 | $7.50 |
| Solder | [Solder](https://a.co/d/edvPC0x) | 2 | g | $0.12 | $0.24 |

### Total
**$192.23**

---
## Purchase List

This is the shopping list. It contains the items you'll need to buy, often in packages that include more parts than the project requires.

### Electronics

| Item | Location | Quantity | Unit Cost | Total Purchase Cost |
| :--- | :--- | :--- | :--- | :--- |
| [12V 2.1mm x 5.5mm DC Power Jack Adapter (4-pack)](https://a.co/d/751q0LK) | Amazon | 1 | $3.97 | $3.97 |
| [18650 Battery Case Holder](https://a.co/d/0sHe8RC) | Amazon | 1 | $7.99 | $7.99 |
| [18650 Rechargeable Batteries with Charger (4-pack)](https://a.co/d/61mFCPq) | Amazon | 1 | $21.98 | $21.98 |
| [3.5mm Female Mount Jack (3-pack)](https://a.co/d/40ZtWEH) | Amazon | 1 | $6.99 | $6.99 |
| [3.5mm Male Jack Connector (2-pack)](https://a.co/d/iWRQpHo) | Amazon | 1 | $5.49 | $5.49 |
| [33' 20 AWG 3-Conductor Electrical Wire](https://a.co/d/fJsRZCa) | Amazon | 1 | $15.99 | $15.99 |
| [Compact Slide Switch](https://a.co/d/2EBehJg) | Amazon | 1 | $8.99 | $8.99 |
| [Dupont Connector Kit (600 pcs)](https://a.co/d/eYwAEnl) | Amazon | 1 | $9.99 | $9.99 |
| [Greartisan DC 12V 30RPM Gear Motor](https://a.co/d/9EDaZ5f) | Amazon | 1 | $15.99 | $15.99 |
| [L298N H Bridge Stepper Motor Driver](https://a.co/d/d2QPwzO) | Amazon | 1 | $2.50 | $9.99 |
| [Micro Limit Switch (1-pack)](https://a.co/d/icHqxsF) | Amazon | 1 | $3.99 | $3.99 |
| [PCB Boards (32 pcs)](https://a.co/d/8yXHcdF) | Amazon | 1 | $6.99 | $6.99 |
| [Raspberry Pi Pico H - Pico with Headers Soldered](https://www.adafruit.com/product/5525) | Adafruit | 1 | $5.00 | $5.00 |
| [RGB 5mm Tri-Color LEDs](https://a.co/d/4jlZoVg) | Amazon | 1 | $8.99 | $8.99 |
| [Tactile Push Button Switches (180 pcs)](https://a.co/d/5Mcb5Zq) | Amazon | 1 | $8.99 | $8.99 |

### Fasteners & Hardware

| Item | Location | Quantity | Unit Cost | Total Purchase Cost |
| :--- | :--- | :--- | :--- | :--- |
| [3/8"-16 Zinc Plated Coarse Thread Hex Nut (8-pack)](https://www.menards.com/main/hardware/fasteners-connectors/nuts/hex-jam-nuts/grip-fast-reg-blue-zinc-grade-2-coarse-thread-hex-nuts/zhn38-8/p-1444421582846-c-8915.htm) | Menards | 1 | $1.05 | $1.05 |
| [3/8" Zinc Plated Flat Washer (24-pack)](https://www.menards.com/main/hardware/fasteners-connectors/washers-spacers/flat-washers/grip-fast-reg-3-8-grade-2-a307-zinc-flat-washer-24-count/15073/p-1444439719658-c-8945.htm) | Menards | 1 | $1.68 | $1.68 |
| [Assorted Nuts and Bolts Kit (720 pcs)](https://www.amazon.com/720pcs-Metric-Assortment-Yellow-Plated/dp/B0BYNLV7YG?ref_=ast_sto_dp&th=1) | Amazon | 1 | $29.99 | $29.99 |
| [M3 Standoff Kit (320 pcs)](https://a.co/d/gYZp2mI) | Amazon | 1 | $9.99 | $9.99 |
| [M5 Screws and T Nuts Kit (420 pcs)](https://a.co/d/blOClPc) | Amazon | 1 | $15.99 | $15.99 |
| [M6 x 1mm Nylon Lock Nuts (35 pcs)](https://a.co/d/dPlYyLJ) | Amazon | 1 | $5.68 | $5.68 |

### Structural & Mechanical

| Item | Location | Quantity | Unit Cost | Total Purchase Cost |
| :--- | :--- | :--- | :--- | :--- |
| [1/2" x 3-13/16" Zinc Extension Spring](https://www.menards.com/main/hardware/fasteners-connectors/specialty-fasteners/springs/midwest-fastener-reg-1-2-x-3-13-16-zinc-extension-spring-1-count/88121/p-1444440197466-c-9553.htm) | Menards | 2 | $2.39 | $4.78 |
| [1-1/4" O.D. Cross-Connector Pipe Clip (10-pack)](https://a.co/d/65sJAJZ) | Amazon | 1 | $22.99 | $22.99 |
| [2-1/2" Soft Rubber Swivel Caster Wheel w/ 3/8"-16 x 1-1/2" threaded swivel stem](https://www.menards.com/main/hardware/casters-furniture-hardware/casters/shepherd-hardware-reg-2-1-2-soft-rubber-swivel-caster-wheel/9340m/p-1444442245967-c-13090.htm?exp=false) | Menards | 3 | $4.49 | $13.47 |
| [3/4" x 10' SDR 21 PVC Plain End Pressure Pipe](https://www.menards.com/main/plumbing/pipe-fittings/pvc-pipe-fittings/sdr21-pvc-pressure-pipe/pvc200070600hc/p-1444426399617-c-8571.htm?missingVariation=true) | Menards | 2 | $4.29 | $8.58 |
| [3/4" x 48" Round Poplar Dowel](https://www.menards.com/main/doors-windows-millwork/dowels-wooden-pins-plugs/madison-mill-round-poplar-dowels/436578/p-1444438758494-c-12188.htm) | Menards | 1 | $3.59 | $3.59 |
| [3/4" Socket Sch 40 PVC 90-Degree Elbow](https://www.menards.com/main/plumbing/pipe-fittings/pvc-pipe-fittings/nibco-reg-socket-schedule-40-pvc-90-degree-elbow/f01680d/p-1444449163717-c-8571.htm?exp=false) | Menards | 10 | $0.67 | $6.70 |
| [3/4" Socket Sch 40 PVC Cap](https://www.menards.com/main/plumbing/pipe-fittings/pvc-pipe-fittings/nibco-reg-socket-schedule-40-pvc-cap/f01890d/p-1444449177939-c-8571.htm?exp=false) | Menards | 3 | $0.81 | $2.43 |
| [3/4" Socket Sch 40 PVC Tee](https://www.menards.com/main/plumbing/pipe-fittings/pvc-pipe-fittings/nibco-reg-socket-schedule-40-pvc-tee/f01790d/p-1444449168936-c-8571.htm?exp=false) | Menards | 14 | $0.86 | $12.04 |
| [300mm 2020 T Slot Aluminum Extrusions (4 pcs)](https://a.co/d/22snyCf) | Amazon | 1 | $17.99 | $17.99 |
| [4" Zip Ties (200-pack)](https://a.co/d/fQBFUen) | Amazon | 1 | $3.99 | $3.99 |
| [5mm x 135mm Hex Shaft (4-pack)](https://www.revrobotics.com/5mm-Hex-Shafts/) | REV Robotics | 1 | $16.99 | $16.99 |
| [6mm Flange Shaft Coupler (5-pack)](https://a.co/d/dtI1bwZ) | Amazon | 1 | $11.99 | $11.99 |
| [QUICK FIST Mini Clamp 5/8" - 1-3/8" (2-pack)](https://www.amazon.com/dp/B006NOC8Q6?th=1) | Amazon | 2 | $8.95 | $17.90 |
| [Rubber Bands](https://a.co/d/6Yn3jlO) | Amazon | 1 | $4.94 | $4.94 |
| [SUNLU PLA+2.0 Filament (1kg spool)](https://a.co/d/5zXOyYR) | Amazon | 1 | $19.99 | $19.99 |

### Consumables

| Item | Location | Quantity | Unit Cost | Total Purchase Cost |
| :--- | :--- | :--- | :--- | :--- |
| [All-Purpose Pipe Cement and Purple Primer Pack - 4 oz](https://www.menards.com/main/plumbing/plumbing-installation-repair/pipe-cements-cleaners-primers/oatey-reg-all-purpose-cement-and-purple-primer-handy-pack-4-oz/302505/p-1958440145915521-c-8530.htm) | Menards | 1 | $9.99 | $9.99 |
| [Solder](https://a.co/d/edvPC0x) | Amazon | 1 | $5.99 | $5.99 |
| [20 AWG Wire](https://a.co/d/efYaxqC) | Amazon | 1 | $14.99 | $14.99 |
| [Wire Heat Shrink Tubing Kit (900 pcs)](https://a.co/d/6wIdCTN) | Amazon | 1 | $6.59 | $6.59 |

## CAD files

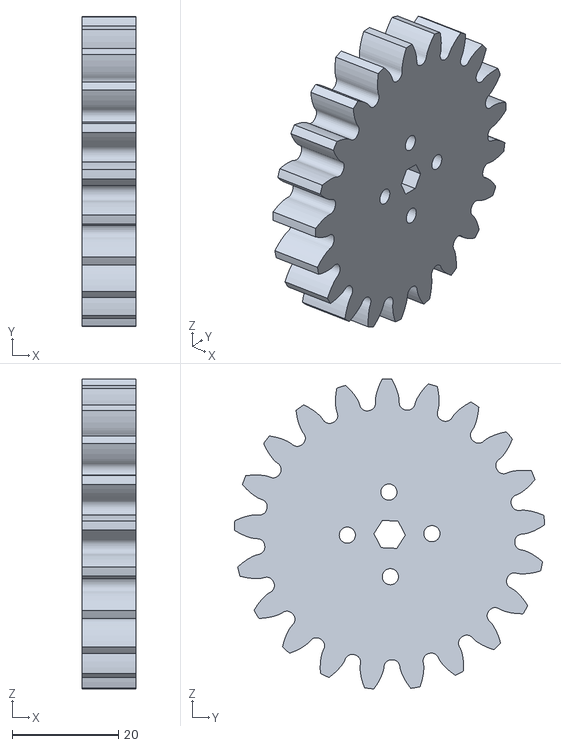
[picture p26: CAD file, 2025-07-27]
3d-models/stl/full-gear-2.stl
10.2 x 58.4 x 58.3

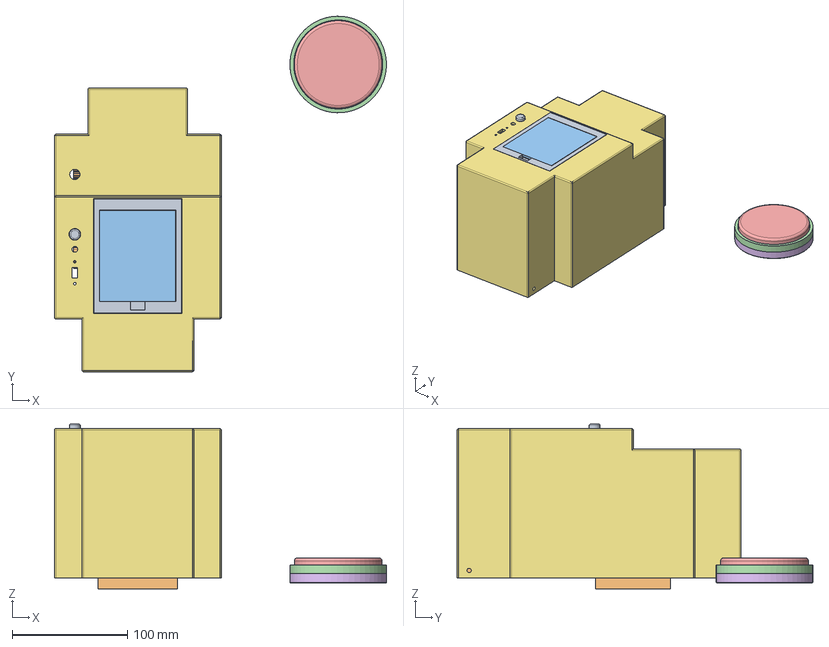
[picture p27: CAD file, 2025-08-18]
3d-models/soccer-launcher.step
288.1 x 308.6 x 143.0 mm
Plunger Spring Lock
Launcher Base
Electronic Base
Half Gear x 2
Gear Spacer x 2
Long Gear Spacer
Pawl
Pawl Axle
Band Anchor
Battery Case
Full Gear x 2
Battery Lid
Launch Button Case
Launch Button Top
Launch Button Base
Casing
Off Button Base
Off Button Top
Bottom Spacer

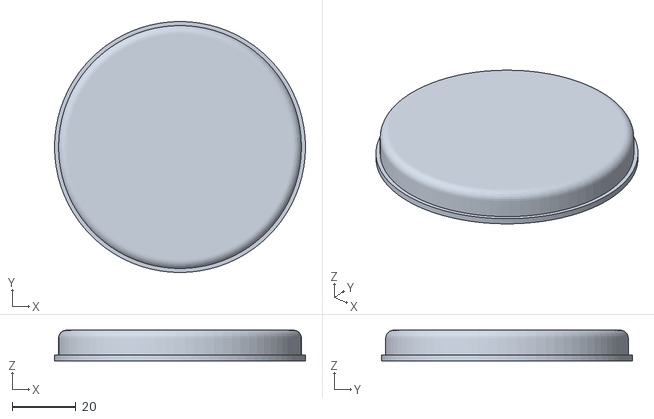
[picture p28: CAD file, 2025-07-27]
3d-models/stl/launch-button-top.stl
78.7 x 78.7 x 9.65

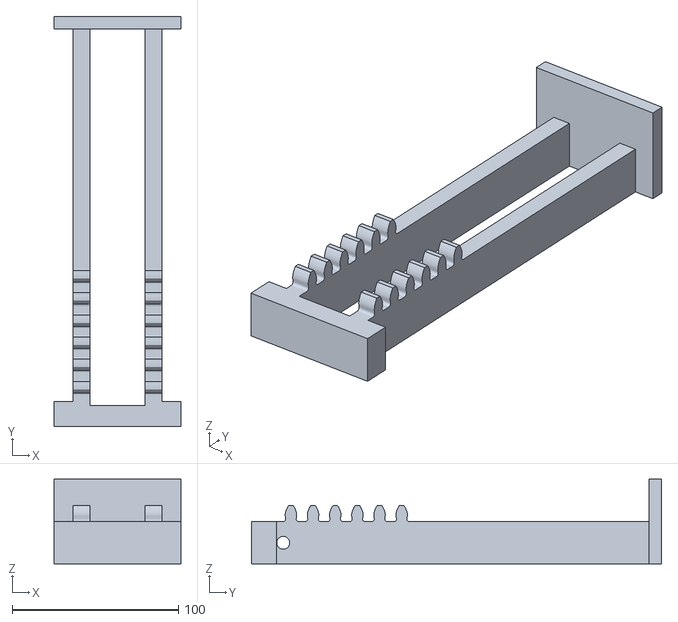
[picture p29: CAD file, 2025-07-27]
3d-models/stl/plunger.stl
76.2 x 246.4 x 51.0

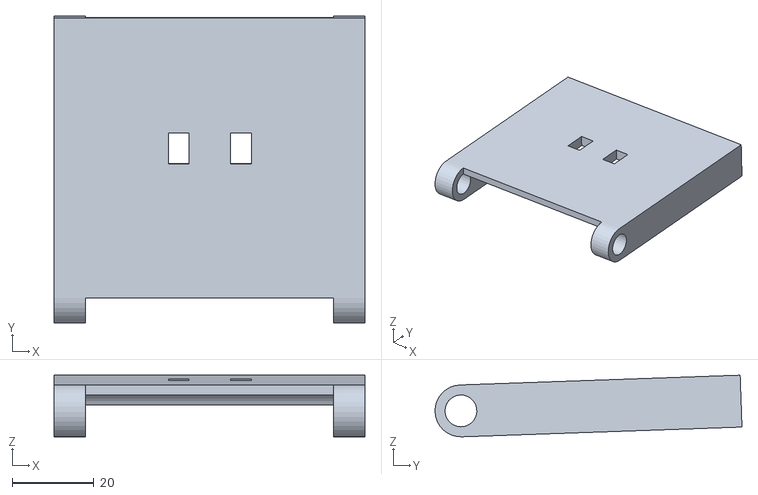
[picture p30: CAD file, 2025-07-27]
3d-models/stl/pawl.stl
76.0 x 75.1 x 15.1

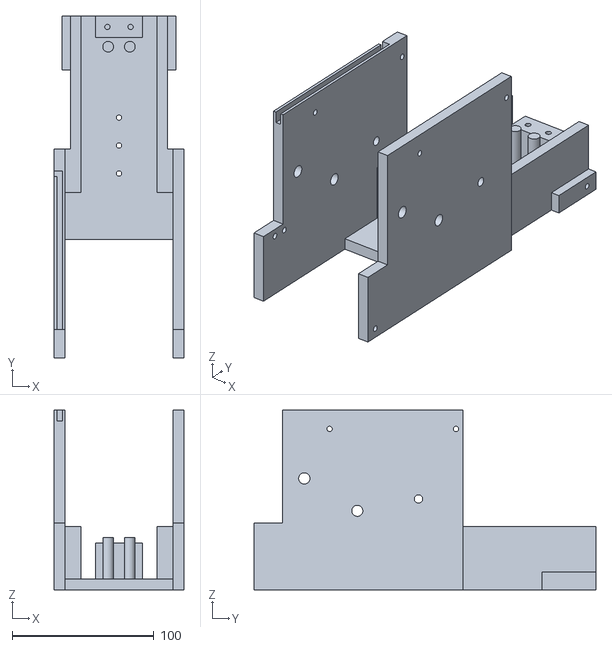
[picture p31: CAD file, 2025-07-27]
3d-models/stl/launcher-base.stl
91.4 x 241.1 x 127.0

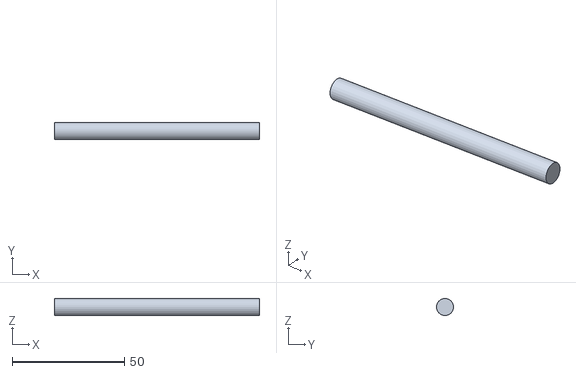
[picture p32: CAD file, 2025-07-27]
3d-models/stl/band-anchor.stl
91.4 x 7.59 x 7.60

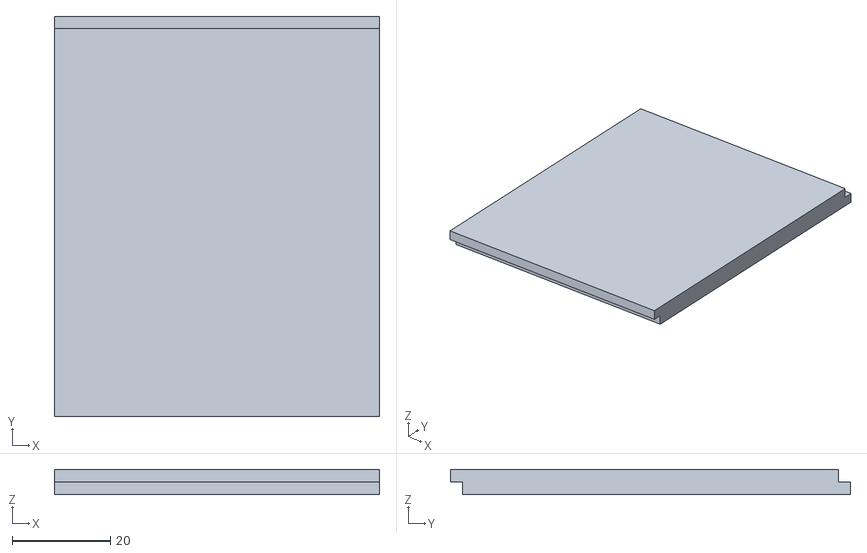
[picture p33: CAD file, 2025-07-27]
3d-models/stl/battery-lid.stl
66.0 x 81.3 x 5.08

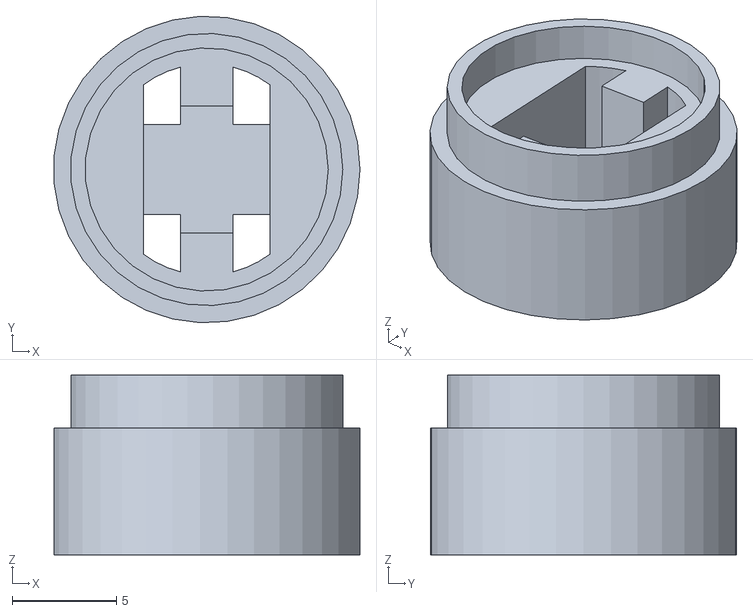
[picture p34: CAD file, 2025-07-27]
3d-models/stl/off-button-base.stl
14.7 x 14.7 x 8.64

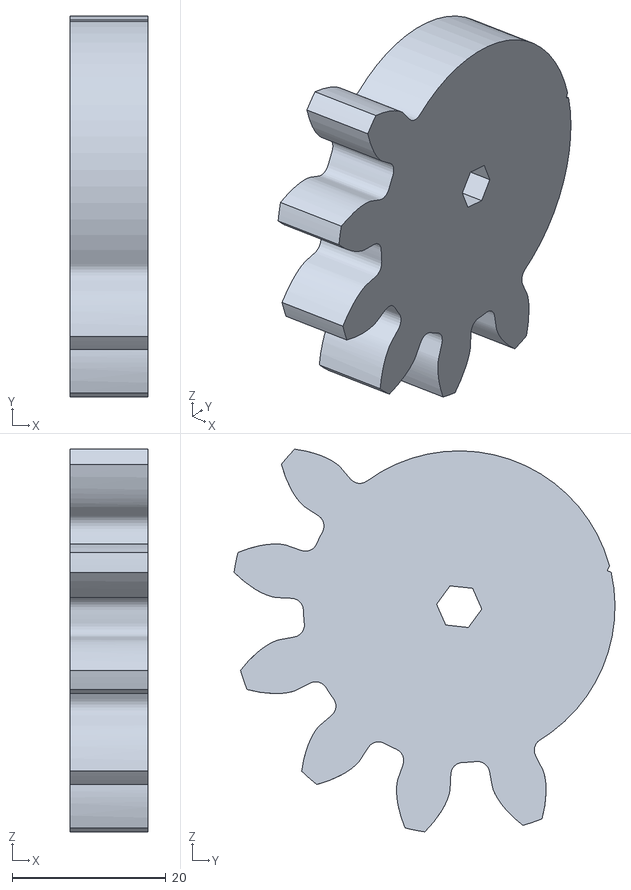
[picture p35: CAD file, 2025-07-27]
3d-models/stl/half-gear-2.stl
10.2 x 49.6 x 49.8

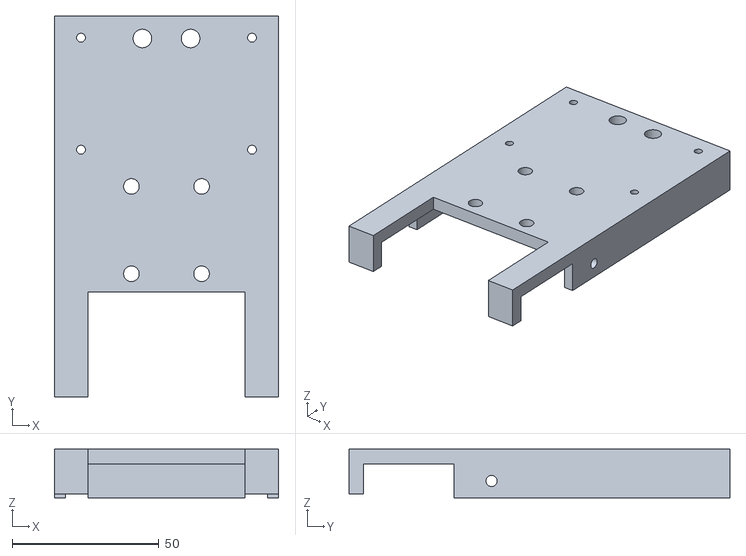
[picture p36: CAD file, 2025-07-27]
3d-models/stl/electronics-base.stl
76.2 x 129.5 x 16.5

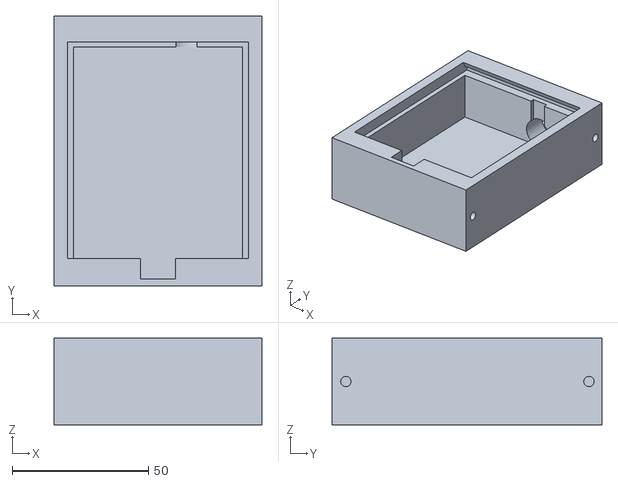
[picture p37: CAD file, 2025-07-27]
3d-models/stl/battery-case.stl
76.2 x 99.1 x 31.8

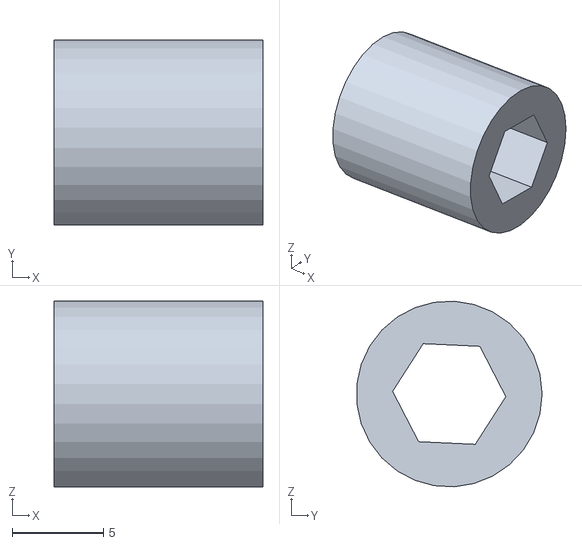
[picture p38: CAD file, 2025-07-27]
3d-models/stl/gear-spacer-2.stl
11.4 x 10.1 x 10.1

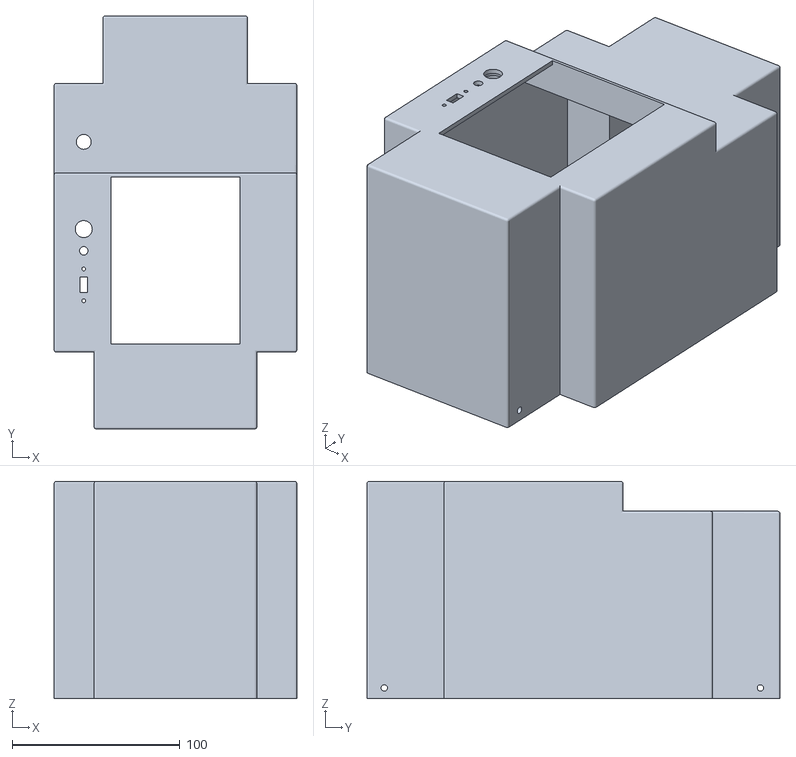
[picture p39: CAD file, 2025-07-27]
3d-models/stl/casing.stl
144.8 x 246.4 x 129.5

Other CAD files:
3d-models/stl/full-gear-1.stl
3d-models/stl/pawl-axle.stl
3d-models/stl/half-gear-1.stl
3d-models/stl/gear-spacer-1.stl
3d-models/soccer-launcher.3mf
3d-models/stl/bottom-spacer.stl
3d-models/stl/launch-button-base.stl
3d-models/stl/launch-button-case.stl
3d-models/stl/off-button-top.stl
3d-models/stl/plunger-spring-lock.stl

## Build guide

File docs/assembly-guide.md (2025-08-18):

---
layout: default
title: Assembly Guide
---
# Assembly Guide

This guide provides detailed, step-by-step instructions for fabricating and assembling all components of the wheelchair soccer launcher.

Assembled Wheelchair Soccer Launcher

### **Table of Contents**

1. **[Before You Begin](#before-you-begin)**  
2. **[Cart Assembly](#cart-assembly)**  
3. **[3D Print Fabrication](#3d-print-fabrication)**
4. **[Electronics Assembly](#electronics-assembly)**  
5. **[Raspberry Pi Pico Programming](#raspberry-pi-pico-programming)**
6. **[Mechanical Assembly](#mechanical-assembly)**

## Before You Begin

This section outlines all the tools and parts you'll need to gather before starting the build.

### Bill of Materials (BOM)

A complete list of all project components and their purchase links can be found using the links below.

* **[bill-of-materials.md](/bill-of-materials.md)**
* **[bill-of-materials.xlsx](/bill-of-materials.xlsx)**

### Tool List

| Tool | Specifications | Notes |
| :---- | :---- | :---- |
| Screwdriver | 3mm phillips head | For various assembly tasks |
| 3D Printer | Minimum 256x256x256mm build volume | To fabricate the custom parts |
| Hand Tap | 5mm tap size | For creating threads in plastic |
| Saw | \- | For cutting wood dowels and PVC pipe |
| PVC Pipe Cutter | \- | A saw will work, but a cutter is easier |
| Soldering Iron | \- | For electronics assembly |
| Tape Measure | \- | For measurements |
| Dial Caliper | \- | For precise measurements |
| Superglue | \- | For permanently bonding small parts |
| Micro USB cable | \- | For programming Raspberry Pi Pico |
| Heat Gun | \- | For wire heat shrink |
| Hex Keys | 1.5mm, 2.5mm, 3mm size | For socket head screws |
| Wire Tools | Wire Stripper, Wire Cutter, Hand Crimper | For all electronics wiring. |
| Hand drill | 1/8", 5/32”, 3/8" drill bit | For drilling holes in PVC and wood. |
| Wrenches | \- | For tightening M5, M6, and 3/8" nuts and bolts. |

## Cart Assembly

This section details how to build the PVC cart that attaches to the wheelchair and funnels the ball to the launcher.

Assembled PVC Cart

### Step 1: Cut PVC Pipes

Using a saw or PVC pipe cutter, cut the 3/4" PVC pipe into the following lengths:

| Length | Quantity |
| :---- | :---- |
| 36” | 2 |
| 20” | 2 |
| 11” | 4 |
| 5” | 1 |
| 2” | 23 |

### Step 2: Assemble the Main Frame

Gather the PVC Tee and 90° Elbow fittings and the cut pipe sections. Assemble the four sub-frames as shown in the diagram below.

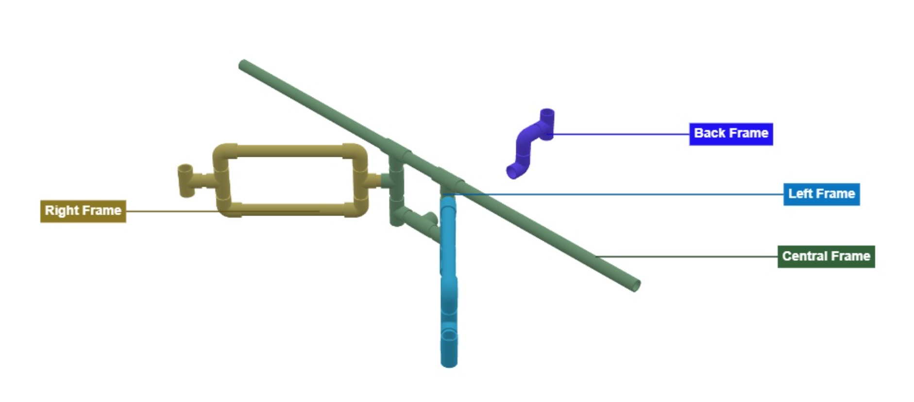
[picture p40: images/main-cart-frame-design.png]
Main Cart Frame Design

*Design mockup created using [Crafty Amigo](https://www.craftyamigo.com/)*

| Part Description | Central Frame | Left Frame | Right Frame | Back Frame | Total |
| :---- | ----- | ----- | ----- | ----- | ----- |
| 3/4" Tee PVC | 7 | 3 | 3 | 1 | 14 |
| 3/4" 90° Elbow PVC | 0 | 4 | 4 | 2 | 10 |
| 3/4" x 2" Tube PVC  | 6 | 6 | 6 | 2 | 20 |
| 3/4" x 11" Tube PVC  | 0 | 2 | 2 | 0 | 4 |
| 3/4" x 20" Tube PVC  | 2 | 0 | 0 | 0 | 2 |
| 3/4" x 5" Tube PVC  | 1 | 0 | 0 | 0 | 1 |

**Assembly Notes:**

* **Dry Fit First:** Assemble the entire cart without glue first to ensure all parts fit correctly.  
* **Angles:** The Tee fitting on the Central Frame that connects to the Back Frame should be parallel to the ground. The Left and Right frames should extend out from the Central Frame at a 45-degree angle.  
* **Glue Later:** Once you have confirmed the fit, disassemble, apply PVC primer and cement, and reassemble each joint for a permanent bond. 

### Step 3: Create the Three Cart Wheels

This step covers creating and attaching the three caster wheels to the Left, Right, and Back Cart Frames.

Cart Wheel

1. Cut three 1-inch pieces from the **3/4" Wood Dowel**.  
2. Center one dowel piece inside a **PVC Cap** and drill a 3/8" hole through the cap and the dowel.  
3. Insert the threaded stem of a caster wheel through the hole in the PVC cap and dowel.  
4. On the inside of the cap, place a **3/8" Flat Washer** over the threaded stem and secure it with a **3/8" Hex Nut.**  
5. Insert one of the remaining **3/4" x 2" PVC Pipes** into the cap.  
6. Repeat this process for all three wheels.  
7. Connect the assembled cart wheels to the designated open PVC tees on the Right, Left, and Back frames. 

### Step 4: Attach the Aluminum Extrusion

Aluminum Extrusion

1. Drill a hole on both sides of the back frame’s elbow joint and the center frame’s horizontal tee joint. The holes should be parallel to the ground, 0.4" from the edge, and drilled with a 5/32” bit.  
2. Use a 5mm hand tap to thread each hole.  
3. Screw an **M5 x 10mm Screw** into each hole and attach a **T-Nut** to the inside, leaving it loose.  
4. Align the T-nuts and slide the aluminum extrusion into both joints, then tighten the screws completely.

### Step 5: Create the Two Wheelchair Grips

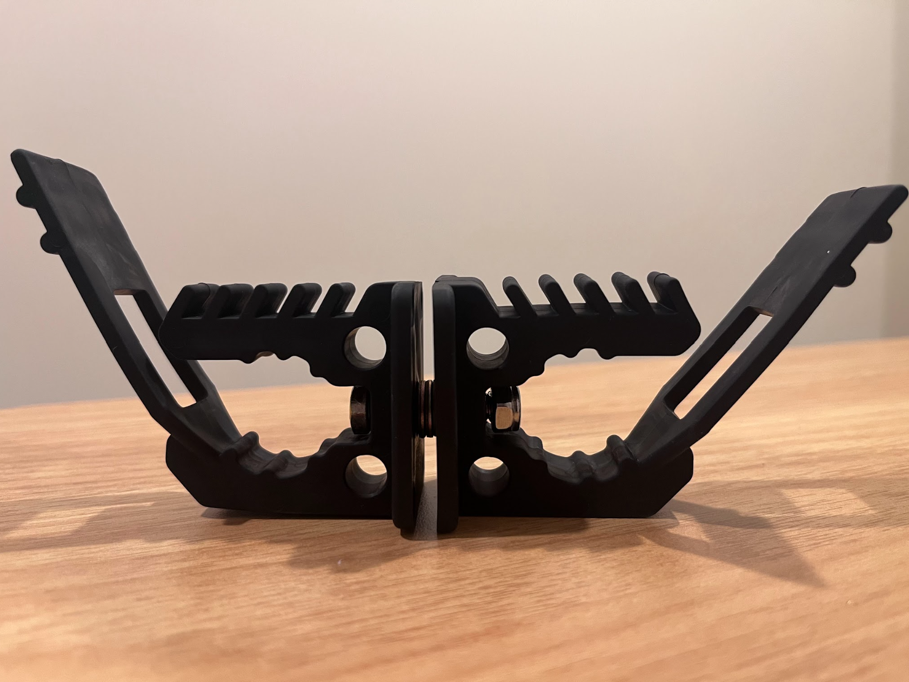
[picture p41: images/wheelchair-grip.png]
Wheelchair Grip


1. Take two **QUICK FIST Mini Clamps**.  
2. Slide an **M6 x 30mm Bolt** completely through one clamp, with the bolt head on the clamp's interior.  
3. Place three **M6 Flat Washers** on the end of the bolt.  
4. Slide the bolt through the back of the second QUICK FIST Mini Clamp.  
5. Secure the assembly with a **Nylon Lock Nut**, tightening it enough to allow the clamps to turn with some resistance.  
6. Repeat this process for the second grip

### Step 6: Attach the Two Wheelchair Arms

Cart Arm

1. Take the two **3/4" x 36” PVC Pipes** and position one end of each on top of and perpendicular to the **20” PVC Pipes** on the center frame.  
2. At each intersection, use a **Cross Connector Pipe Clip** to join the pipes. The nuts should be tight enough to prevent side-to-side movement but still allow for rotation.  
3. Attach one of the previously assembled Mini Clamp grips to the other end of each 36” PVC pipe.

### Final Cart Assembly

Assembled PVC Cart

## 3D Print Fabrication

This section details how to print and prepare the custom components for the launcher assembly. Component names used here correspond to the `.step` filenames. The parts were designed in Fusion 360, and the `.f3d` file is available for modifications.

3D Printed Components

### Step 1: Print Each component

First, download the design files from the [3D Models](/3d-models/) folder. Files are available in `.step`, `.f3d`, `.3mf`, and individual `.stl` formats.

**Recommended Print Settings**

| Setting | Value |
| :---- | :---- |
| Printer | Bambu Lab P1S |
| Resolution | 0.2mm |
| Supports | Yes |
| Rafts | No |
| Infill Pattern | Gyroid |
| Filament | SUNLU PLA+ 2.0 |

**Part-Specific Settings**

Use the following infill percentages for different components (the specific Bambu presets are also noted).

| Parts | Infill | Slicer Preset |
| :---- | :---- | :---- |
| Band Anchor, Casing, Plunger, Plunger Spring Lock | 40% | 0.2mm Bambu Strength Preset |
| All Other Components | 15% | 0.2mm Bambu Standard Preset |

**Note:** It's recommended to lower the print speed when printing the Casing due to the thin walls

### Step 2: Tap M5 holes

For reliable connections, you'll need to tap threads into several of the printed parts. First, pre-drill each hole with the 5/32” drill bit, then create threads using a 5mm hand tap.

**Launcher Base**:

Launcher Base Drill Locations

* Drill and tap the middle **3 holes** completely through the bottom.  
* Drill and tap the front **2 holes** to a depth of 3/4" (do not drill through).

**Electronics Base & Launcher Base**:

Electronics Base Drill Locations

* Drill and tap **2 holes** on either side through both parts to a depth of 0.3". Do not go entirely through the launcher base.

**Launcher Base & Battery Case**:

Battery Case Drill Locations

* Drill and tap **4 holes** at each corner through both parts to a depth of 0.75".

**Casing & Launcher Base**:

Casing Drill Locations

* Drill and tap **4 holes** at each lower corner through both parts to a depth of 0.3". Do not go entirely through the launcher base.

### Step 3: Break in Components

Some parts require a "break-in" to ensure smooth operation. Manually move the following components back and forth to reduce friction.

Breaking in Plunger

* Ensure the **Plunger** can slide freely within the launcher base.

Breaking in Axles

* Check that the **Pawl Axle** (black) can rotate freely in its hole in the launcher base.  
* Confirm the **Band Anchor** (white) fits properly into its slot in the launcher base.

Breaking in Hex Axle

* Check the **5mm Hex Axle** can rotate freely in its hole in the launcher base.

Breaking in Gears

* Make sure the **Gears** can slide along the 5mm Hex Axle. This should require some force and not be loose

3. ## Electronics Assembly

This section details how to assemble, mount, and wire the electronic components. For clarity, follow the wiring diagram and pictures provided. It's helpful to imagine the final placement of the components to cut wires to a suitable length—not too short to be taut, but not so long they become tangled.

### Step 1: Prepare the Main Control Board

This step focuses on mounting the L298N Motor Driver and Raspberry Pi Pico to the PCB, creating the central control unit. 

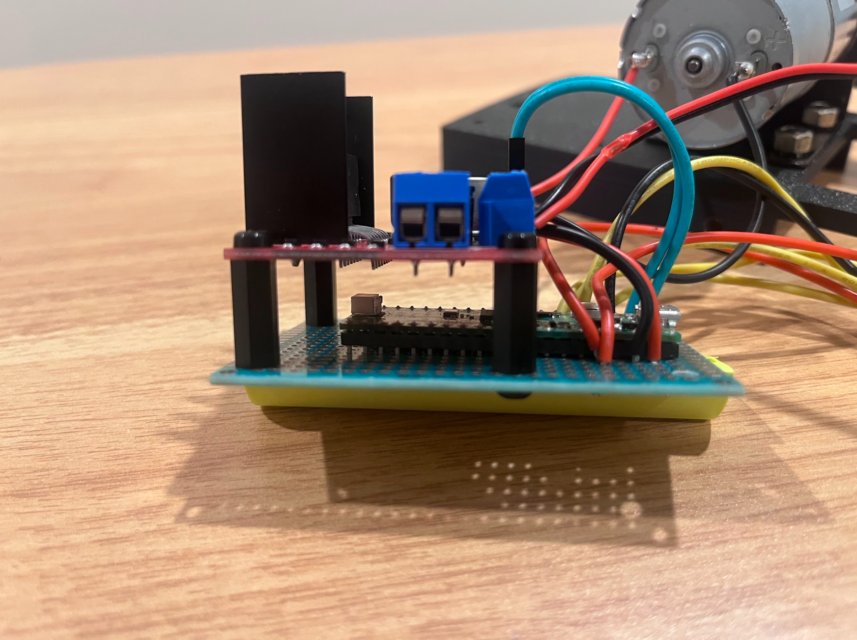
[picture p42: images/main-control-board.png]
Main Control Board


***Please Note:** Ignore the wires in the picture, they will be added later.*

1. **Mount Standoffs to L298N**: Screw the four **M3 x 15mm Double-Pass Standoffs** into the corners of the **L298N Motor Driver** using four **M3 x 12mm Standoff Screws**.  
2. **Position on PCB**: Place the L298N assembly onto the **5cm x 7cm PCB Board**. The L298N's heat sink should face one edge of the board.  
3. **Drill Mounting Holes**: Mark and drill four holes with a **1/8" drill bit** where the standoffs will connect to the PCB. Two of these holes should be corner holes. Ensure these corner holes align with the mounting holes on the  
    **3D Printed Electronics Base**. Drill holes in the other two corners of the PCB as well.  
4. **Secure L298N**: Fasten the L298N to the PCB by screwing two **M3 x 6mm screws** through the board and into the two non-corner standoffs. The corner holes will be used later to mount the entire board.  
5. **Place Raspberry Pi Pico**: Insert the **Raspberry Pi Pico** into the PCB so its micro-USB port faces the edge opposite the L298N motor driver.

### Step 2: Mount the Motor

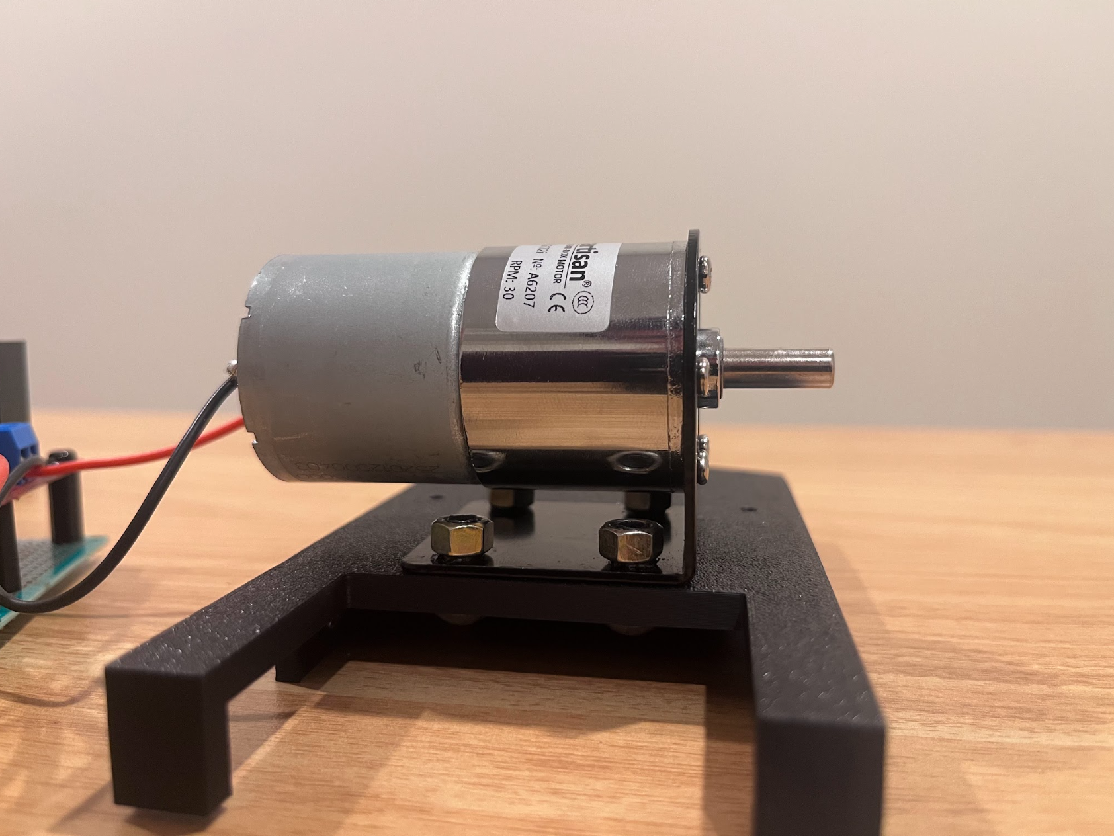
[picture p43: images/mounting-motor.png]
Mounting Motor


1. Attach the **DC Motor** to the **Motor Mounting Bracket**.  
2. Place the motor and bracket onto the **3D Printed Electronics Base**. The motor shaft should face the right (the two clip arms facing back).  
3. Secure the assembly by inserting four **M5 x 12mm screws** up through the bottom of the electronics base and into the bracket. Tighten with four **M5 nuts**.

### Step 3: Mount the Limit Switch

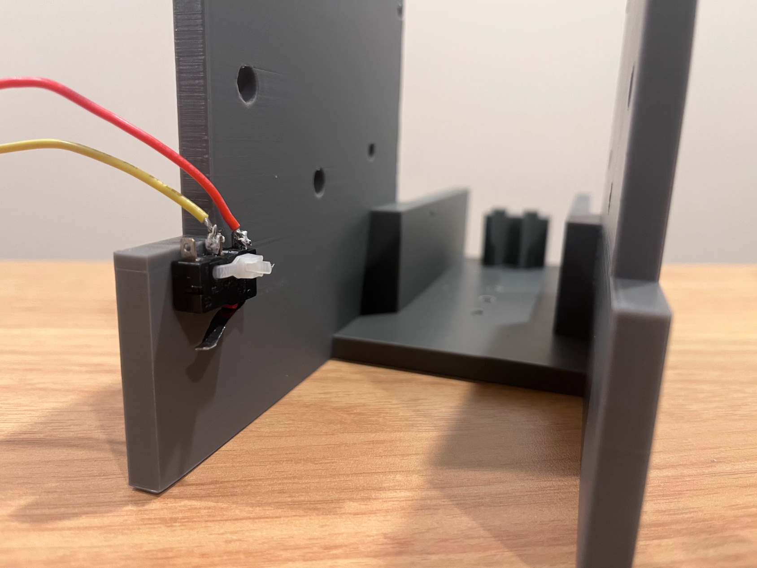
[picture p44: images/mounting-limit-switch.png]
Mounting Limit Switch

   
***Please Note:** Ignore the wires in the picture, they will be added later.*

1. Position the **Limit Switch** on the back of the **3D Printed Launcher Base**.  
2. Use a zip tie fed through the two small holes to secure the switch. The zip tie should sit flush inside the outer wall of the print.  
3. Cut the excess zip tie.

### Step 4: Assemble the Launch Button

This step covers building the external launch button.

Launch Button Electronics

1. **Place Components**:  
   1. Insert a **6x6x9.5mm Tactile Push Button** into the center of the **3D Printed Launch Button Base**.  
   2. Place a **3.5mm Female Mount Jack** through the hole in the side of the base.  
2. **Solder Internal Wires**: Solder two short wires to connect the bottom and left pins of the female jack to the two pins on the tactile button.

Launch Button Cable

3. **Prepare the Cable**: Solder a **3.5mm Male Plug** to each end of the **11-foot 3-Conductor Wire**. You only need to connect the red-to-red and black-to-black wires. Use 4mm heat shrink on the individual connections and 6mm heat shrink over the entire cable end.

Launch Button

4. **Final Button Assembly**:  
   1. Place the **3D Printed Launch Button Top** over the tactile button and press down to snap it in place.  
   2. Apply super glue around the edge of the female jack and push it firmly into its hole.  
   3. Apply super glue around the top edge of the button base and press the **3D Printed Launch Button Case** on top, aligning the rounded portion with the female jack.

### Step 5: Wire the L298N Components

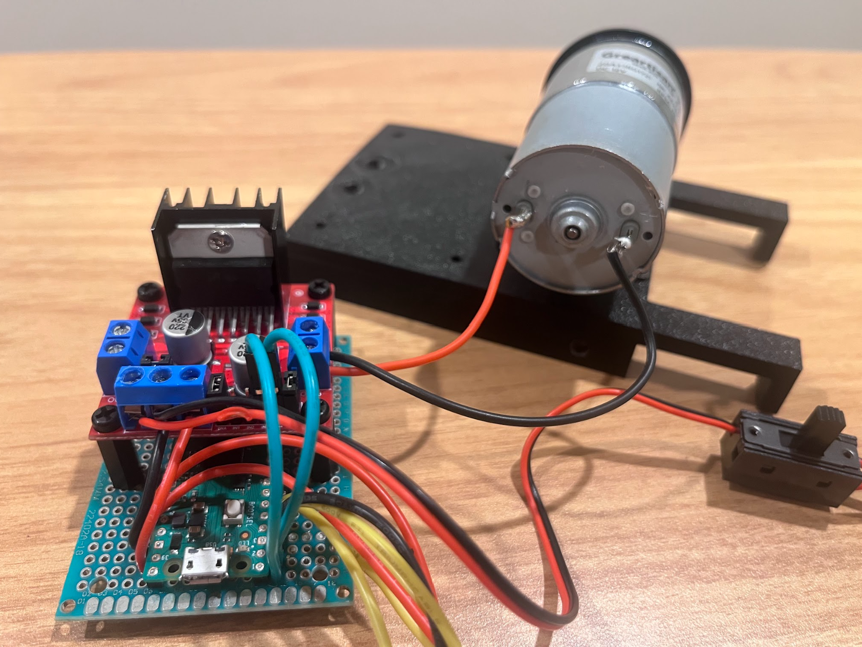
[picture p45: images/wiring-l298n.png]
Wiring L298N

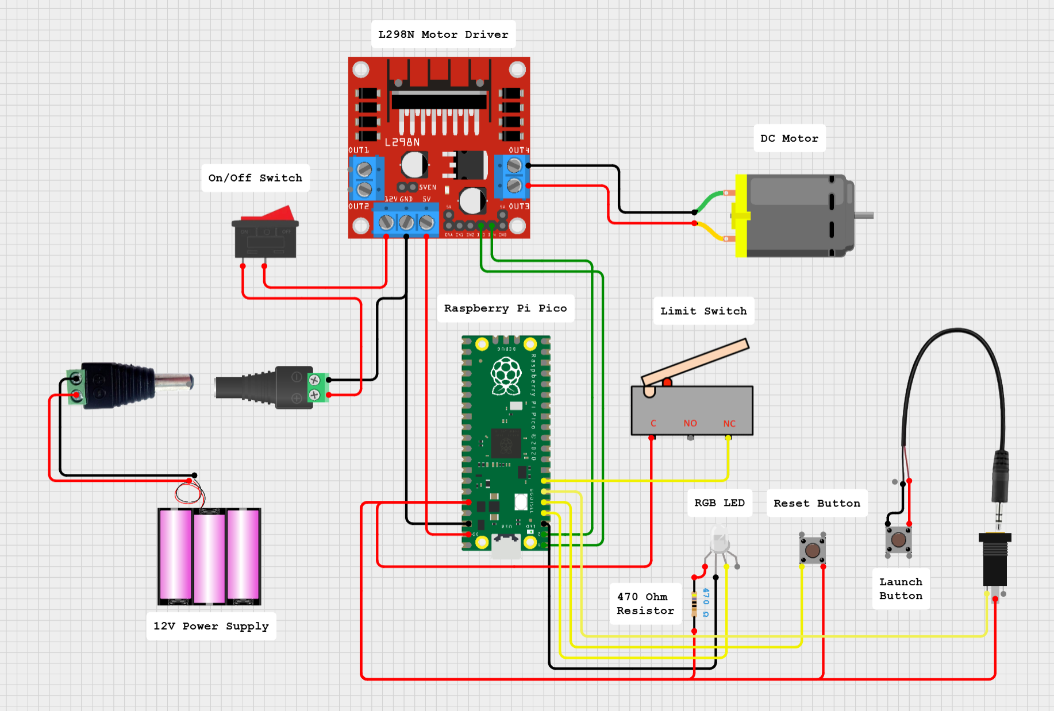
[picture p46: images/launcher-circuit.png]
Launcher Circuit

*Circuit image created using [Cirkit Designer](https://www.cirkitstudio.com/)*

***Note on Wire Lengths:** For the best fit, orient the L298N/PCB board in its final position—mounted in front of the motor with the heat sink facing right. The approximate lengths provided in the following steps are based on this layout.*

1. **Motor to L298N**:  
   1. Solder a \~2.3" wire from **OUT3** on the L298N to the left pin of the DC motor.  
   2. Solder a \~3.8" wire from **OUT4** on the L298N to the right pin of the motor.  
2. **L298N to Pico (Signal)**:  
   1. Crimp female pin connectors onto two \~2.5" wires and insert them into a **2-Pin Housing Connector**.  
   2. Solder the wire from **IN3** on the L298N to **Pin 1** of the Pico.  
   3. Solder the wire from **IN4** on the L298N to **Pin 2** of the Pico.  
3. **Power Switch to Components**:  
   1. On the **On/Off Switch**, connect the red wire from the **NO** terminal to the **12V** terminal on the L298N. Connect the black wire to the **GND** terminal.  
   2. Connect the red and black wires from the **COM** terminal to the **\+** and **\-** terminals, respectively, of the **5.5mm Female DC Barrel Jack**.  
   3. Zip tie the unused **NC** wire to the **COM** and cut excess  
4. **L298N to Pico (Power)**:  
   1. Connect a \~1.5" wire from the **5V** terminal on the L298N to **Pin 39** on the Pico.  
   2. Connect a \~1.5" wire from the L298N's **GND** terminal to **Pin 38** on the Pico.

### Step 6: Wire the Casing Components

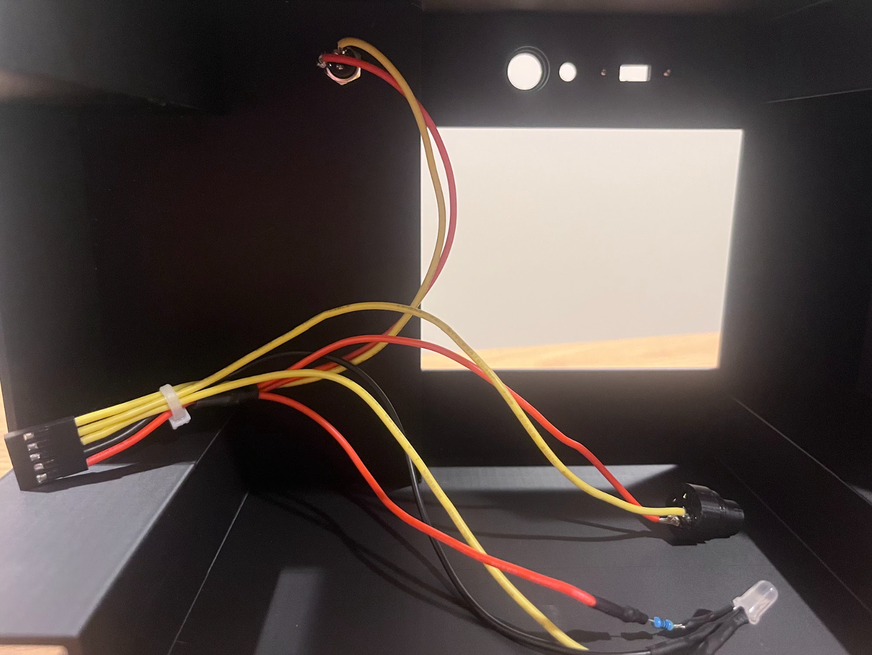
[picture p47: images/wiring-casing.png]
Wiring Casing

Launcher Circuit

This step prepares the **connector cable** for the components that will be mounted in the outer casing.

***Wiring Note:** To easily orient the connector, use distinctly colored wires. This guide will refer to the wires by number based on the picture: Wire 1 (Red), Wire 2 (Black), and Wires 3-5 (Yellow).*

1. **Mount Jack**: Insert the **3.5mm Female Mount Jack** into the front-most hole of the 3D printed casing and secure it with its nut.  
2. **Prepare Reset Button**: Insert a **6x6x11mm Tactile Push Button Switch** into the **Off Button Bottom**, then press the **Off Button Top** onto it.  
3. **Create Connector Cable**:  
   1. Cut seven \~6.5" wires and one \~1.5" wire.  
   2. Crimp female pin connectors onto four of the long wires and the one short wire. Insert these five wires into a **5-Pin Housing Connector**.  
   3. Solder the short wire to the three remaining long wires to create a shared connection.  
4. **Solder Components to the Connector Cable**:  
   1. **RGB LED**: Solder the longest pin (Pin 2\) to the black wire (wire 2). Solder the red pin (Pin 1\) to the 470 Ω resistor, and then solder one of the shared red wires (wire 1\) to the other end of the resistor. Solder the green pin (Pin 3\) to the first yellow wire (wire 3). Cut the blue pin (Pin 4).  
   2. **Reset Button**: Solder another shared red wire (wire 1\) to one pin of the button and the second yellow wire (wire 4\) to the other pin.  
   3. **Mount Jack**: Solder the last shared red wire (wire 1\) to the bottom pin and the last yellow wire (wire 5\) to the left pin.  
5. **Finalize Casing**: Press-fit the 5mm LED and the Reset Button into their holes in the casing. Zip tie the connector cable wires together neatly.

### Step 7: Wire Raspberry Pi Pico Components

This final wiring step connects the limit switch and the casing's connector cable to the main control board.

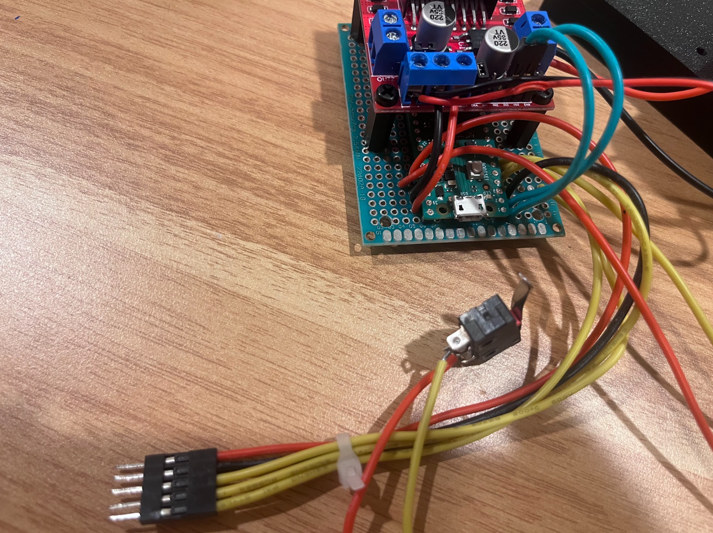
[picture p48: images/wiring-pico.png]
Wiring Pico

Launcher Circuit

***Please Note:** Disregard the soldering mistake in the photo where the yellow wire for Pin 4 is on the edge of the board. Ensure this wire follows the pattern of the others.*

1. **Limit Switch to Pico**:  
   1. Solder two \~10" wires to the **COM** and **NO** pins of the limit switch.  
   2. Route these wires through the channel in the launcher base.  
   3. Solder the **COM** wire to **Pin 36** of the Pico and the **NO** wire to **Pin 7**.  
2. **Casing's Connector Cable to Pico**:  
   1. Create a male-ended connector by cutting five \~5" wires that match the colors of your female connector. Crimp **Male Pin Connectors** onto them and insert them into a **5-Pin Male Housing Connector** in the same color order.  
   2. Solder the wires from the male connector to the Pico as follows: the red wire (1) to **Pin 36**, the black wire (2) to **Pin 3**, the first yellow wire (3) to **Pin 4**, the second yellow wire (4) to **Pin 5**, and the last yellow wire (5) to **Pin 6**.  
   3. Zip tie the wires together neatly.

## Raspberry Pi Pico Programming

### Step 1: Setup MicroPython on the Pico

First, you'll install MicroPython, the programming language used for this project. The easiest way to do this is with the Thonny IDE. Detailed instructions can be found [here](https://projects.raspberrypi.org/en/projects/getting-started-with-the-pico/1).

1. **Download Firmware:** Download the official MicroPython UF2 file for the Raspberry Pi Pico from the [Raspberry Pi documentation page](https://www.raspberrypi.com/documentation/microcontrollers/micropython.html).  
2. **Enter Bootloader Mode:** Unplug your Pico. Press and hold the **BOOTSEL** button on the Pico, and while holding it, plug the Pico into your computer's USB port.  
3. **Copy Firmware:** Release the BOOTSEL button. The Pico will appear as a removable drive named `RPI-RP2`. Drag and drop the `.uf2` file you just downloaded onto this drive. The Pico will automatically reboot.  
4. **Install Thonny:** If you don't have it, download and install [Thonny](https://thonny.org/), a beginner-friendly Python IDE.  
5. **Configure Thonny:** Open Thonny. Go to `Tools > Options` and select the `Interpreter` tab. From the interpreter dropdown, choose **MicroPython (Raspberry Pi Pico)**. The port should be detected automatically. Click `OK`.

### Step 2: Load the Launcher Program

Now you'll copy the project's code onto the Pico.

1. **View the Raw Code:**  
   1. Navigate to the [`main.py`](/micropython-code/main.py) file in the GitHub `micropython-code` folder.  
   2. In the top-right corner of the file view, click the **`Raw`** button. This will open a new browser tab showing only the plain text of the code.  
2. **Copy the Code:**  
   1. Select all the text on the page (you can use `Ctrl+A` on Windows or `Cmd+A` on Mac).  
   2. Copy the selected text to your clipboard (`Ctrl+C` or `Cmd+C`).  
3. **Paste and Save in Thonny:**  
   1. Go back to Thonny and open a new, blank file.  
   2. Paste the code you copied into Thonny's editor (`Ctrl+V` or `Cmd+V`).  
   3. Go to `File > Save copy`. When prompted where to save, select **Raspberry Pi Pico**.  
   4. Name the file exactly **`main.py`** and click `OK`. This is critical, as the Pico is programmed to run this file automatically on startup.

### Step 3: Final Assembly and Testing

This final check verifies that all connections and code are working correctly.

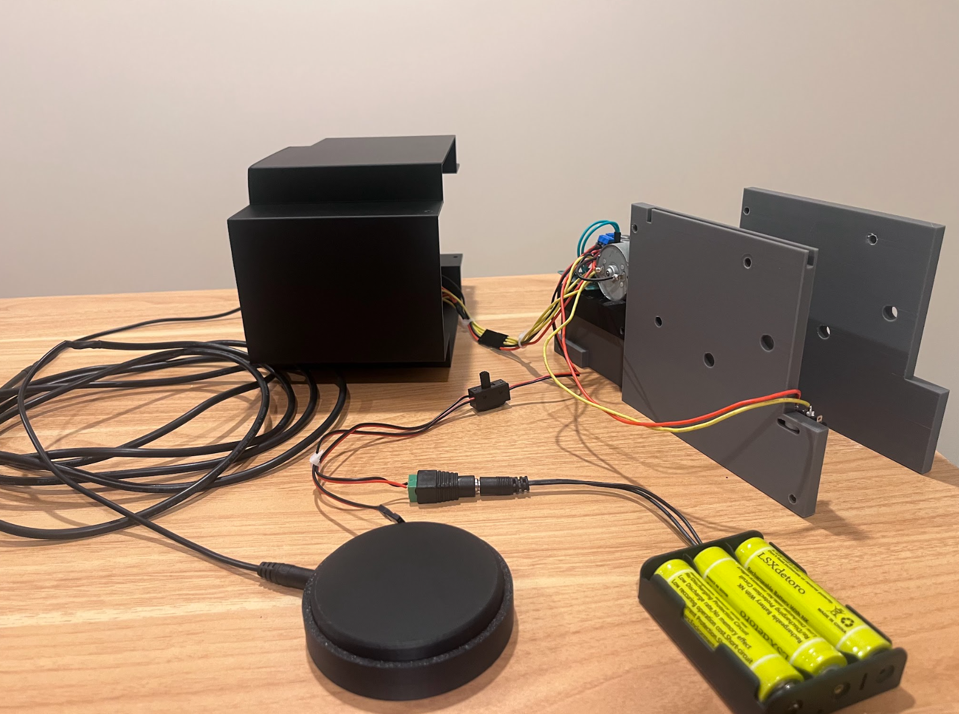
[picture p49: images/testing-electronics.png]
Testing Electronics


1. **Make Connections:**  
   1. Connect the 5-pin **connector cable** from the main casing to the corresponding 5-pin connector on the electronics board.  
   2. Plug one end of the **launch button cable** into the 3.5mm jack on the casing and the other end into the launch button itself.  
   3. Insert three charged **18650 batteries** into the battery case holder and plug its barrel jack into the power port.  
2. **Perform Functional Test:**  
   1. Turn the main power switch to ON.  
      1. **Expected Result:** The LED should turn **green**, and the motor should begin to rotate.  
   2. Press the limit switch on the launcher base.  
      1. **Expected Result:** The motor should **stop**.  
   3. Press the external launch button.  
      1. **Expected Result:** The motor should **rotate again**.  
   4. Press the limit switch again.  
      1. **Expected Result:** The motor should **stop**.  
   5. Press the off button on the casing.  
      1. **Expected Result:** The motor should rotate for half a second, then stop, and the LED should turn **red**.

## Mechanical Assembly

This section details the final assembly of the launcher mechanism and its attachment to the cart.

### Step 1: Attach Launcher Base to Cart

Launcher Base Bottom

1. **Prepare the Launcher Base**: Insert three **M5 x 25mm Bolts** with **M5 Flat Washers** through the three center holes on the bottom of the **3D Printed Launcher Base**.  
2. **Attach Spacer and T-Nuts**: From underneath, slide the **3D Printed Bottom Spacer** over the bolts. Loosely thread on three **M5 T-Nuts**.

Attaching Launcher Base to Cart

3. **Mount to Cart**: Temporarily remove the back frame of the PVC cart. Slide the T-Nuts of the launcher assembly into the channel of the aluminum extrusion. Position the assembly as far forward as it can go, until the PVC frame stops it.  
4. **Secure Launcher**: Firmly tighten the three M5 bolts until the launcher base is secure and cannot move.  
5. **Re-attach Back Frame**: Re-install the back frame of the cart, adjusting the T-nuts as needed to fit.

### Step 2: Install the Plunger

Assembled Plunger

1. **Prep the Plunger**: Slide the **Plunger Lock** halfway through the side of the **Plunger**. Hook both **Extension Springs** onto the lock, ensuring they face the same direction. Slide the lock the rest of the way through until it is flush on both sides.

Launcher Base with Plunger

2. **Insert into Launcher**: Place the plunger assembly into the launcher base. Secure the other end of the springs onto the two vertical poles inside the launcher base.

### Step 3: Mount the Electronics.

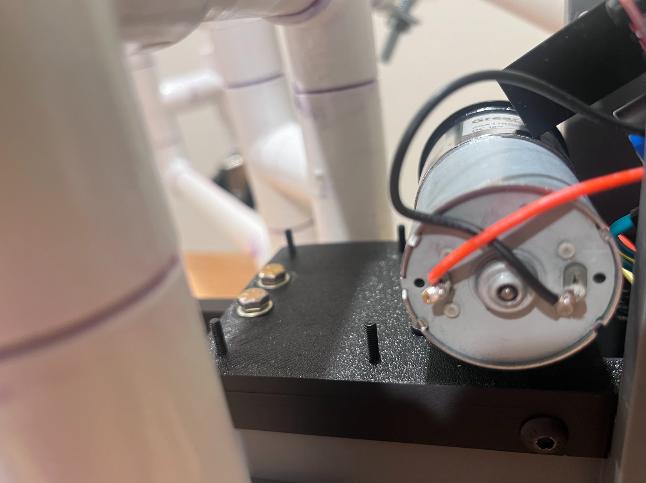
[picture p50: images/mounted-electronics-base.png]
Mounted Electronics Base


1. **Attach Electronics Base**:  
   1. Insert four **M3 x 12mm Standoff Screws** with **M3 Washers** up through the bottom of the **3D Printed Electronics Base**.  
   2. Snap the electronics base onto the launcher base.  
   3. Secure the front with two **M5 x 30mm Bolts** and **M5 Washers**. Do not overtighten, as the plunger must still slide smoothly.  
   4. Secure the sides with two **M5 x 8mm Screws**.

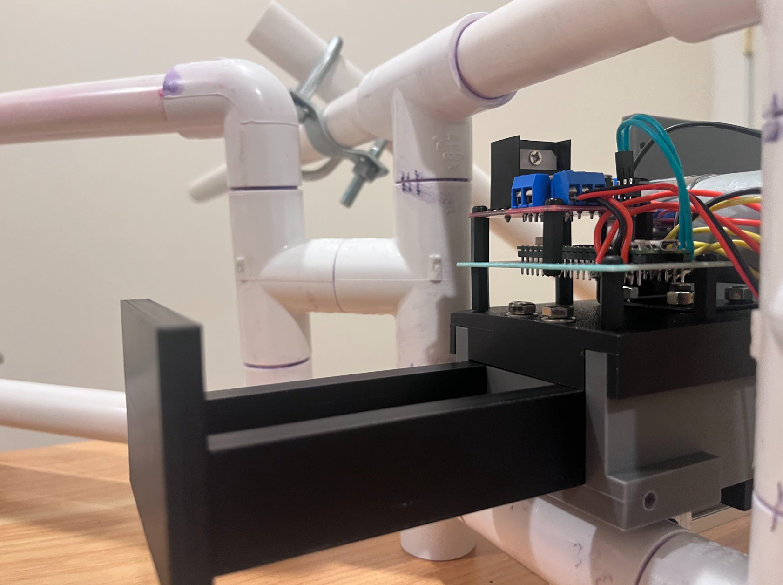
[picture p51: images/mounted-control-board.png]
Mounted Control Board


2. **Mount Control Board**:  
   1. Screw two **M3 (15mm) Double-Pass Standoffs** onto the two holes near the front of the motor. On the other side, screw in two **M3 (15mm \+ 6mm) Single-Head Standoffs**.  
   2. Fasten the **Main Control Board** onto the two single-head standoffs (this should be the side with the L298N heat sink).  
   3. Secure the other side of the board using two **M3 x 6mm Standoff Screws** on the open double-pass standoffs.

Assembled Motor Gear
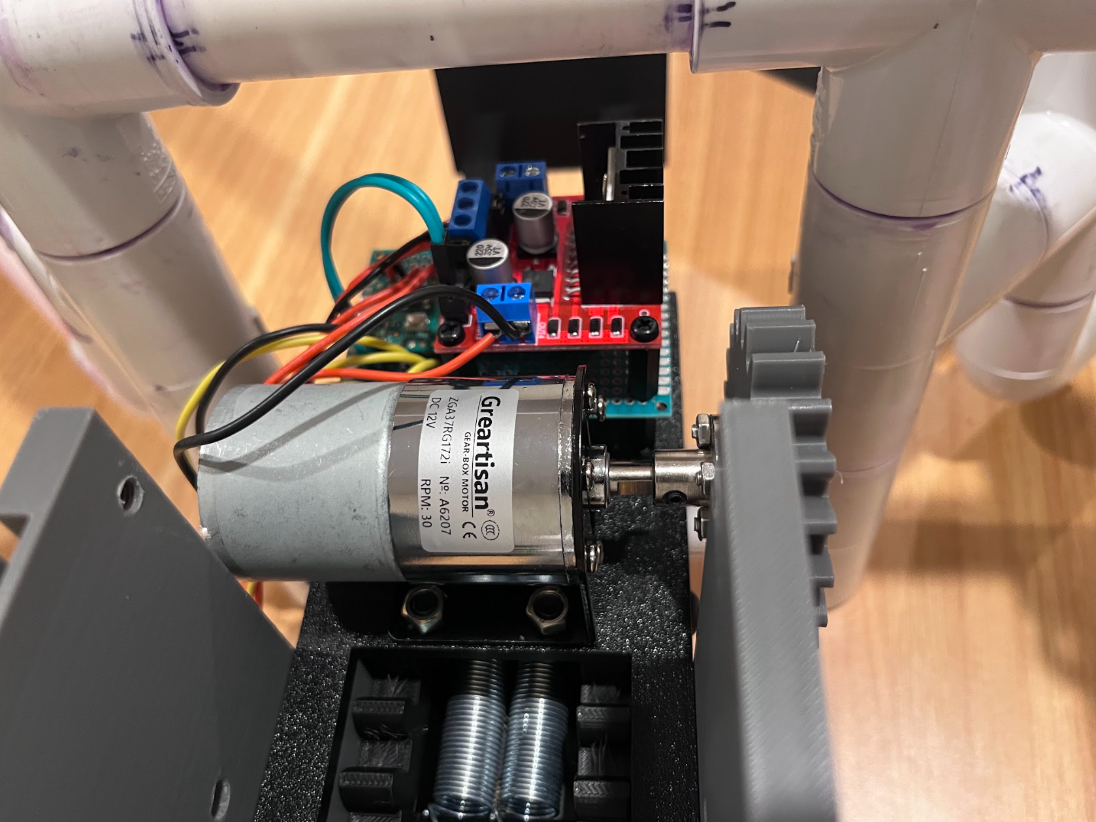
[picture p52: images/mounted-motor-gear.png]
Mounted Motor Gear


3. **Assemble and Mount Motor Gear**:  
   1. Take one of the **3D Printed Full Gears**. Through the recessed side, insert four **M3 x 14mm Socket Head Screws**.  
   2. Fully tighten four **M3 Standoff Nuts** onto the screws.  
   3. Place a **6mm Flange Coupler** (flange facing the gear) over the nuts and secure it with four **M3 Coupler Nuts**.  
   4. Attach the entire gear assembly to the motor shaft, ensuring the gear sits flat against the launcher base wall.  
   5. Lock the coupler onto the flat part of the motor axle with an **M3 Coupler Fastening Screw**.

### Step 4: Install Axles and Battery Case

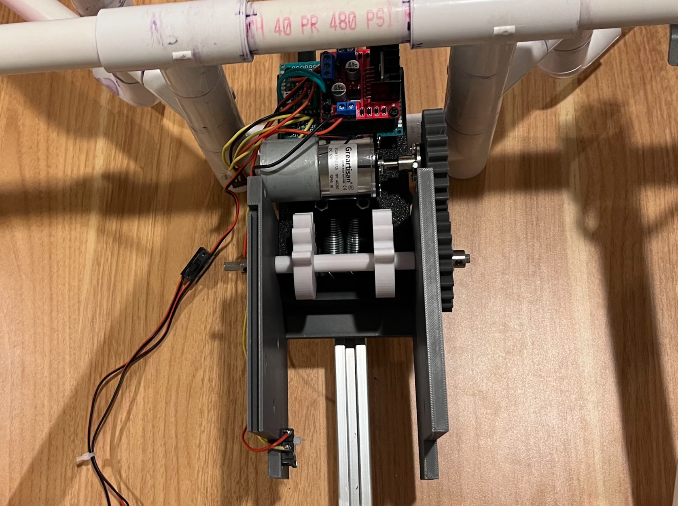
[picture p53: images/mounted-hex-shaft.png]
Mounted Hex Shaft


1. **Assemble Hex Shaft**:  
   1. Insert the **5mm x 135mm Hex Shaft** through the front-most hole in the launcher base.  
   2. From one side, slide on the components in this order: **Spacer**, **Half Gear**, **Long Spacer**, **Half Gear**, **Spacer**. Make sure the half gears have the same orientation.  
   3. Center the shaft so it is even on both sides.  
   4. Attach the other **Full Gear** to one end of the shaft so it meshes with the motor gear.  
   5. Secure both ends of the hex shaft with a **Flange Coupler** and an **M3 Coupler Fastening Screw**.

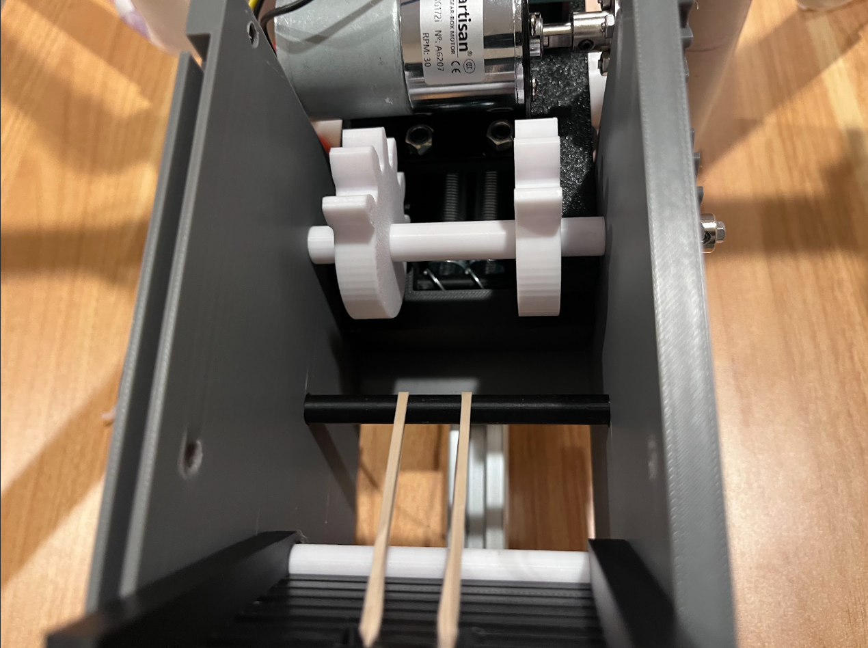
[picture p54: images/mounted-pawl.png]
Mounted Pawl


2. **Install Pawl**:  
   1. Slide the **3D Printed Pawl Axle** through the upper hole in the launcher base and through the **Pawl**.  
   2. Wrap a rubber band through the designated holes on the pawl and secure it to the **Band Anchor**, which is inserted through the lower launcher base hole.

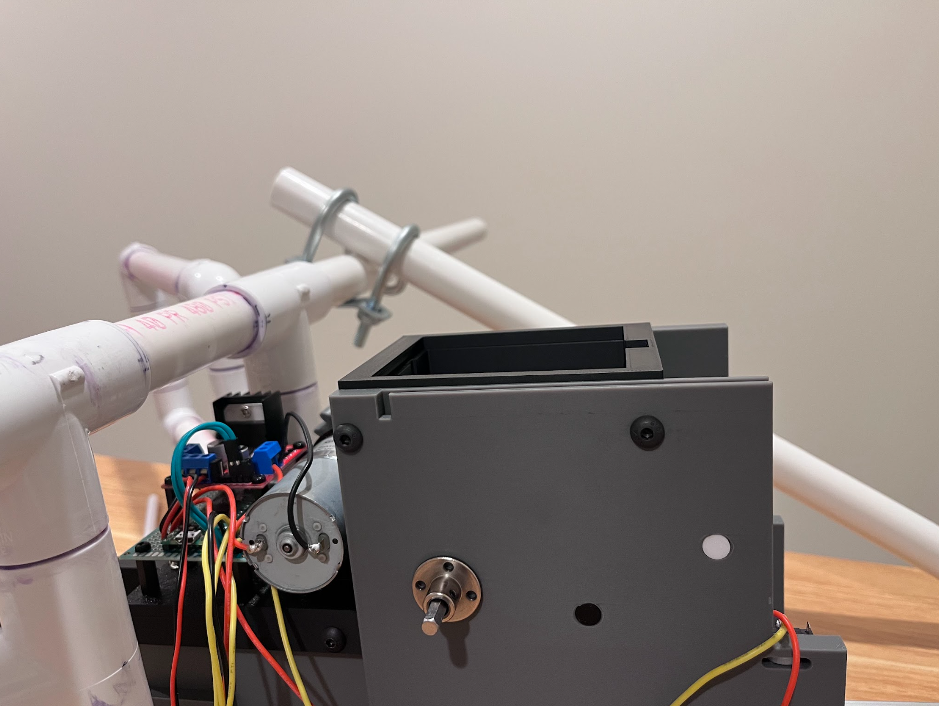
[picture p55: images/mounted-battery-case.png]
Mounted Battery Case

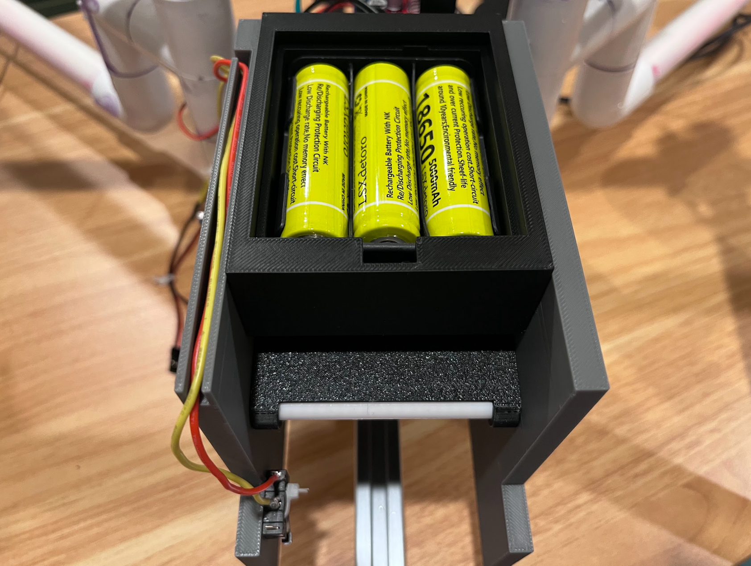
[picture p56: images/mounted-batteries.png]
Mounted Batteries


3. **Mount Battery Case**:  
   1. Attach the **3D Printed Battery Case** to the upper four holes of the launcher base using four **M5 x 14mm Screws**, with the wire port facing the electronics.  
   2. Insert the **18650 Battery Holder** (with three charged batteries) into the printed case.  
   3. Plug the battery holder's barrel jack into the female connector attached to the power switch.

### Step 5: Attach the Launcher Casing

Attached Casing

1. **Disassemble for Fitting**: Temporarily unscrew the two screws holding the aluminum extrusion and slide it off the cart's center frame.  
2. **Fit the Casing**: Gently fit the **3D Printed Casing** over the entire launcher assembly, being careful not to pinch any wires.  
3. **Connect Electronics:** Plug the 5-pin male connector from the main control board into the 5-pin female connector attached to the casing's wiring.  
4. **Secure Casing**: Fasten the casing to the launcher base using four **M5 x 8mm Screws** in the bottom corners.  
5. **Reassemble**: Guide the aluminum extrusion back onto the center frame, adjusting the T-nuts as needed, and tighten the screws to secure it to the PVC cart.

## Final Assembly

Final Assembly 1
Final Assembly 2

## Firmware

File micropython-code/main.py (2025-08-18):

"""
Operates a motorized plunger mechanism for the automatic launcher.

## Cycle of Operation
When the program starts, the LED starts as green.

1.  The motor runs continuously to retract a plunger.
2.  When the plunger is fully retracted, it hits a limit switch, which stops the motor. The system is now armed.
3.  Pressing the launch button runs the motor for a moment to release the plunger.
4.  After launch, the limit switch is released, and the cycle repeats from step 1.

The off button can be pressed at any time to stop the program, turning the
status LED to red.
"""

# -----------------------------------------------------------------------------
## IMPORTS
# -----------------------------------------------------------------------------
from machine import Pin
from time import sleep

# -----------------------------------------------------------------------------
## HARDWARE SETUP (GPIO PINS)
# -----------------------------------------------------------------------------
clockwise_motor = Pin(0, Pin.OUT)               # If motor rotates in wrong direction, set this to 1
counter_clockwise_motor = Pin(1, Pin.OUT)       # Motor control pin
green_led = Pin(2, Pin.OUT)                     # LED (HIGH=green, LOW=red)
off_button = Pin(3, Pin.IN, Pin.PULL_DOWN)      # Button to stop the program
button = Pin(4, Pin.IN, Pin.PULL_DOWN)          # Launch button
switch = Pin(5, Pin.IN, Pin.PULL_DOWN)          # Limit switch for plunger
led = Pin(25, Pin.OUT)                          # Onboard LED on the Pico

# -----------------------------------------------------------------------------
## INITIAL STATE
# -----------------------------------------------------------------------------
clockwise_motor.value(0)
reset = False           # Flag to control the main loop
green_led.value(1)      # Start with the status LED as green

# -----------------------------------------------------------------------------
## MAIN LOOP
# -----------------------------------------------------------------------------
while not reset:
    # --- State 1: Plunger is retracted and hits the LIMIT SWITCH ---
    if switch.value():
        # Stop the motor and onboard LED while waiting for launch
        led.value(0)
        counter_clockwise_motor.value(0)

        # Wait here until the 'launch' button is pressed
        while not button.value():
            sleep(0.1)  # Small delay to prevent high CPU usage
            # Check if the 'off' button is pressed to exit the program
            if off_button.value():
                reset = True
                break

        # Once button is pressed, run motor briefly to release the plunger
        led.value(1)
        counter_clockwise_motor.value(1)
        sleep(0.5)

    # --- State 2: Plunger is retracting ---
    else:
        # Run the motor continuously until the limit switch is hit
        led.value(1)
        counter_clockwise_motor.value(1)

    sleep(0.01) # Short delay to stabilize the loop

# -----------------------------------------------------------------------------
## CLEANUP
# -----------------------------------------------------------------------------
# This code runs after the 'off_button' is pressed.
# Turn everything off to return to a safe state.
led.value(0)
green_led.value(0) # Set status LED to red
counter_clockwise_motor.value(0)

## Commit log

2025-07-27 added pictures and assembly guide; updated bill of materials
    [Bill of Materials.xlsx, band-anchor.stl, battery-case.stl, battery-lid.stl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]
2025-07-28 updated assembly guide
2025-07-28 removed temporary file
    [bill-of-materials.xlsx]
2025-08-18 Create and organize project documentation website
    [bill-of-materials.xlsx, soccer-launcher.step]
